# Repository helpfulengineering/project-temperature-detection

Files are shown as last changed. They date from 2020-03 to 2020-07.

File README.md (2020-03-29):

# Hardware temperature detection project

Project to build a simple, cheap, open source fever detection device. The aim is to allow symptomatic people to be quickly isolated.

On slack channel [#hardware-temperature-detection](https://app.slack.com/client/TUTSYURT3/CVCEV2V0V/thread/CV96HC6DN-1584885987.479600) from [helpfulengineering.slack.com](https://helpfulengineering.slack.com/)

Fast fever detection followed by isolation reduces the spread of infectious diseases.

## User Experience

Journey a user goes through to use the system
Initial idea is represented in the picture, taking the user from the first interface with the device to the result feedback. 
It assumes the mirror alignment but does not go into detail about it yet. 
It also lacks the user experience after the outcome communication. 

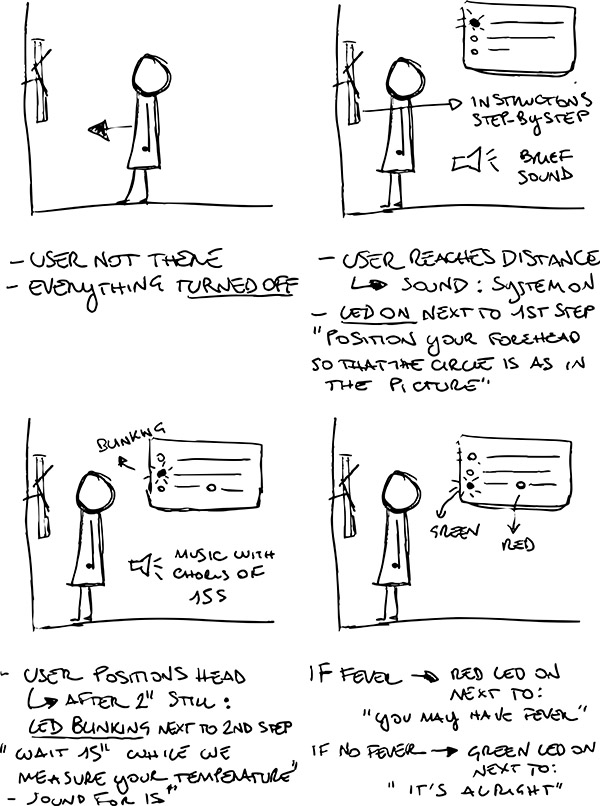
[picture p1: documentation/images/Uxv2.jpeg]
UX


## Functional diagram

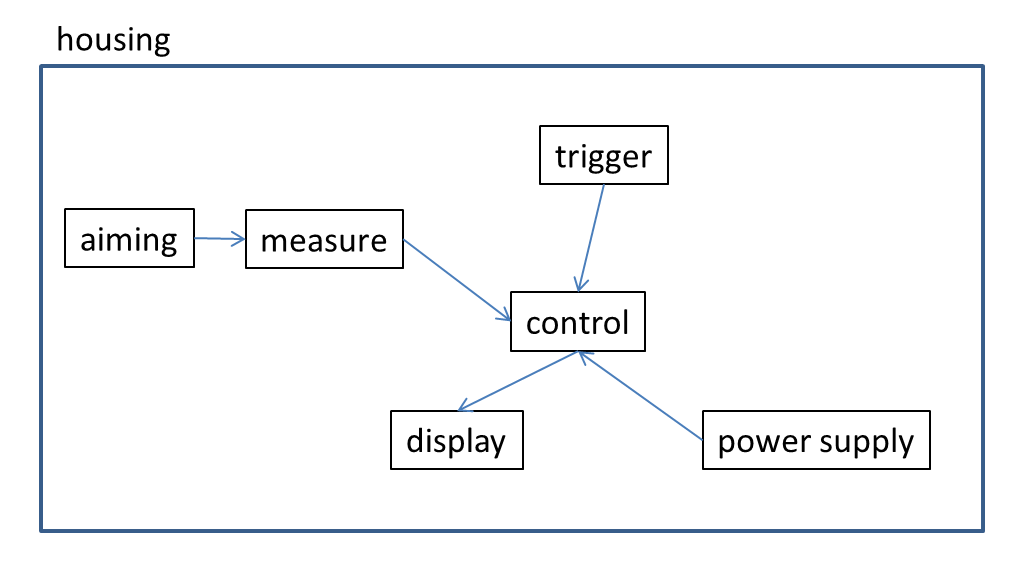
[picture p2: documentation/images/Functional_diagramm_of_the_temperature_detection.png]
diagram


## [Project wiki](https://github.com/helpfulengineering/project-temperature-detection/wiki)

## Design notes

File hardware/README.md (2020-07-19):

# PCB and parts

### parts
- temperature sensor MLX90614
- acoustic range find sensor - generic Hc-SR04
- 10mm LEDs generic
- Arduino UNO

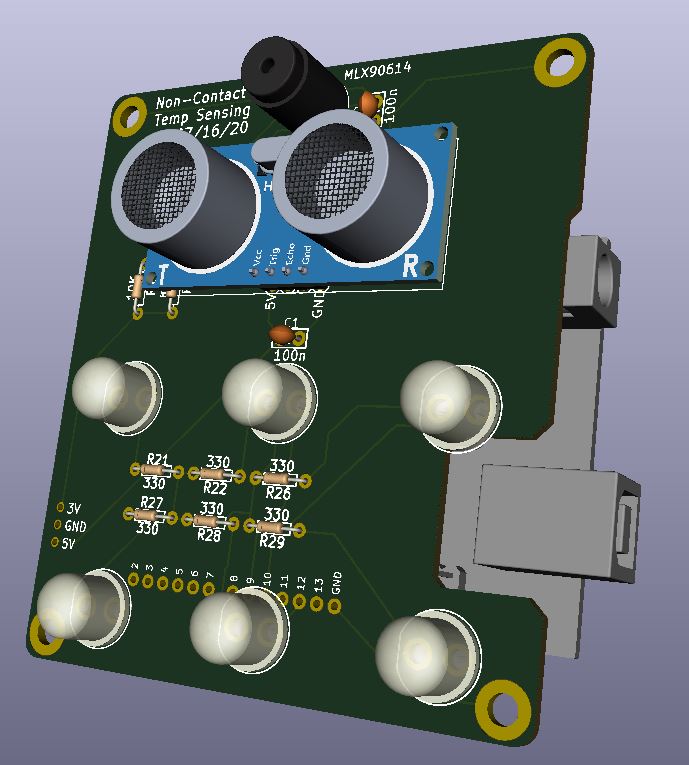
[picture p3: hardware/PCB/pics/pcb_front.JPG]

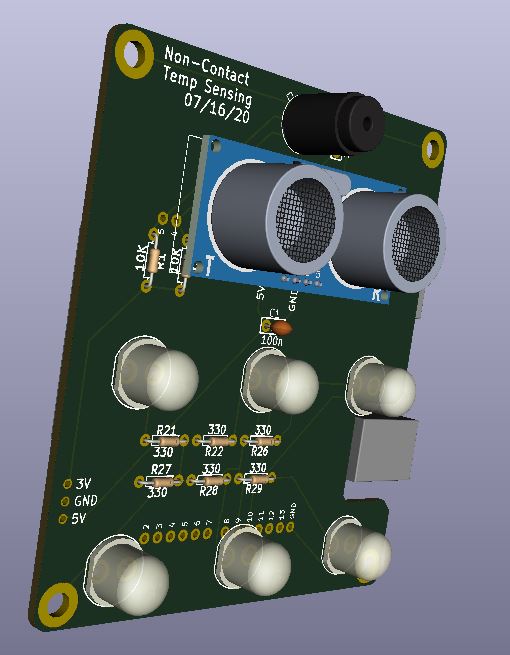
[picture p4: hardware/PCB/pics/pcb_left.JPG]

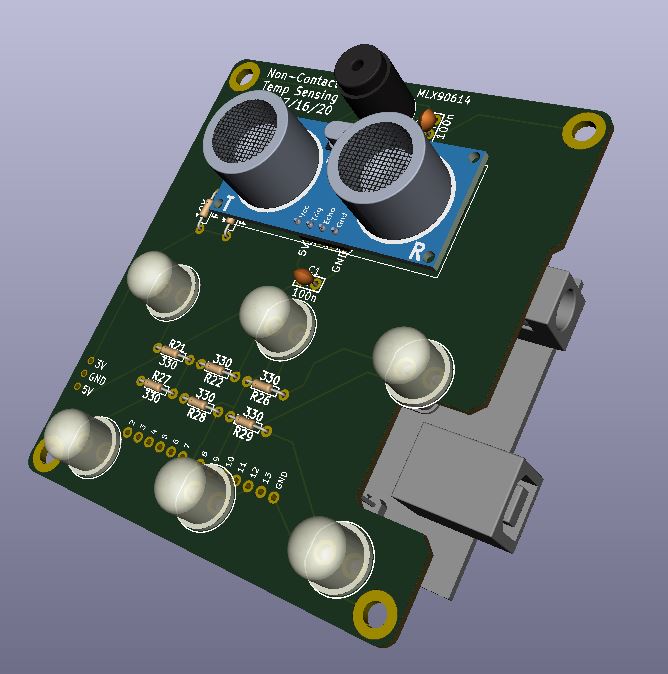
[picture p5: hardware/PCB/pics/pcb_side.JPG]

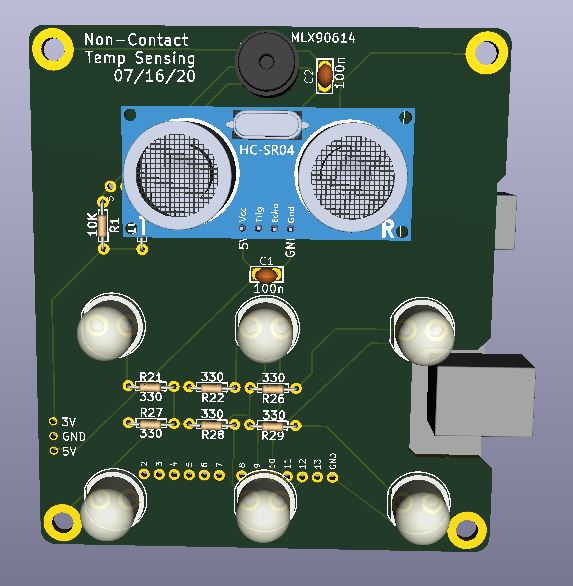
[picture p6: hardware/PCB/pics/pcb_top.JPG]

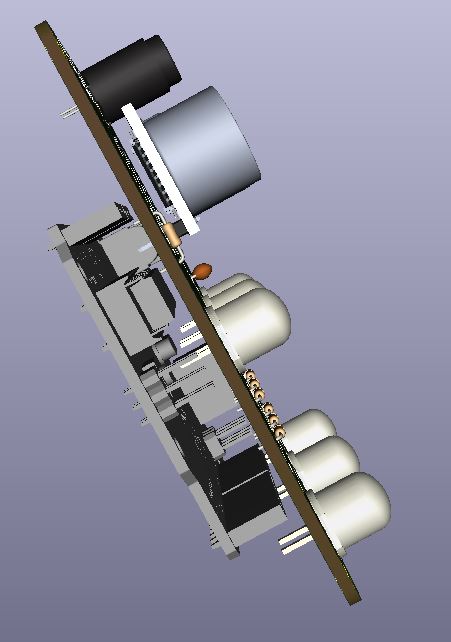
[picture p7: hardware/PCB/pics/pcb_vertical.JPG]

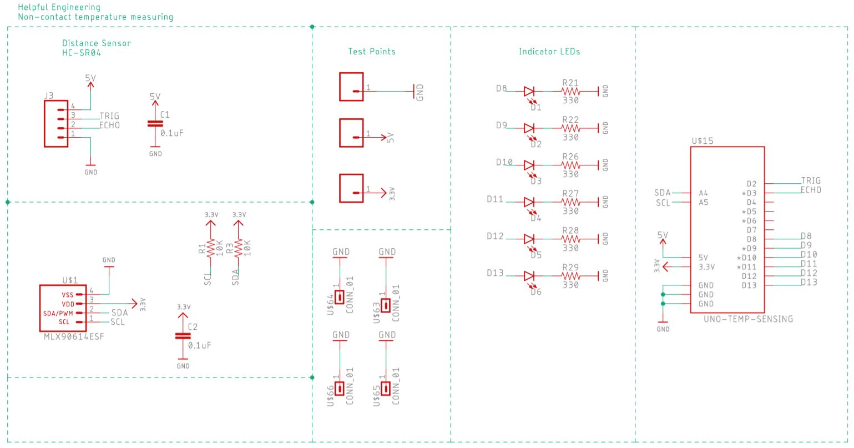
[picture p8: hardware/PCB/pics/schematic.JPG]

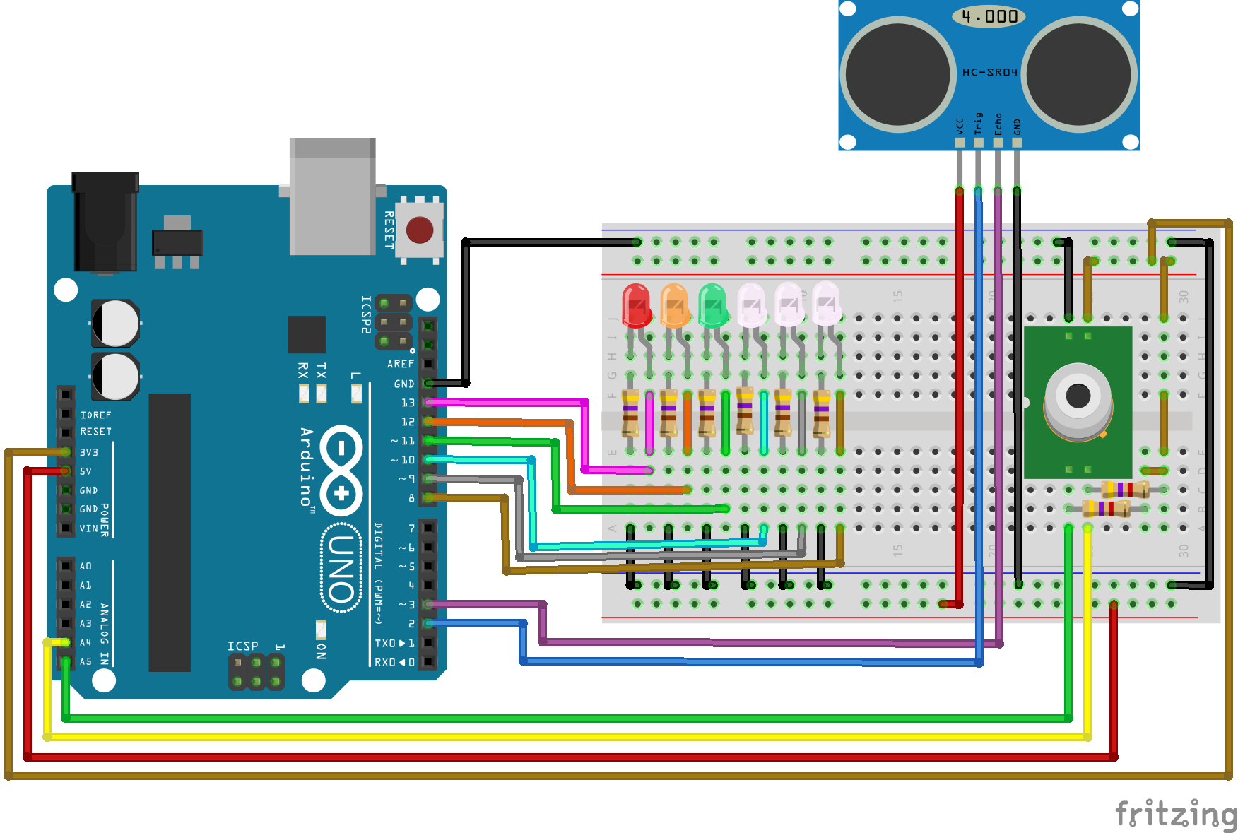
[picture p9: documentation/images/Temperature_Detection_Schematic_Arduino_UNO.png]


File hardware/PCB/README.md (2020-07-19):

# PCB in Eagle

The current printed circuit board was designed in Eagle and imported into kicad for 3d renderings

foo

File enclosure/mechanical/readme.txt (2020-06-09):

Laser cut all parts
Material: Acrylic 
Thickness: 3mm. (1/8" works too)
Adhesive base panel to side panels with acrylic cement or acrylic glue.
On the clear part, the red line is for etching.
All parts were designed to fit on a Glowforge laser cutter

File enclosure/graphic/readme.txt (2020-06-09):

print this on white paper, cut along the red line, laminate it, cut as close to edge as possible. Tape along top and bottom edges against the INSIDE of the clear window (use the etched border of the clear window as a positioning guide).

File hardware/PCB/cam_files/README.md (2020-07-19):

# Hardware temperature detection project - cam files

These are the files required for MFG the PCB. Upload the files to a board house like [JLCPCB.com](https://jlcpcb.com/).

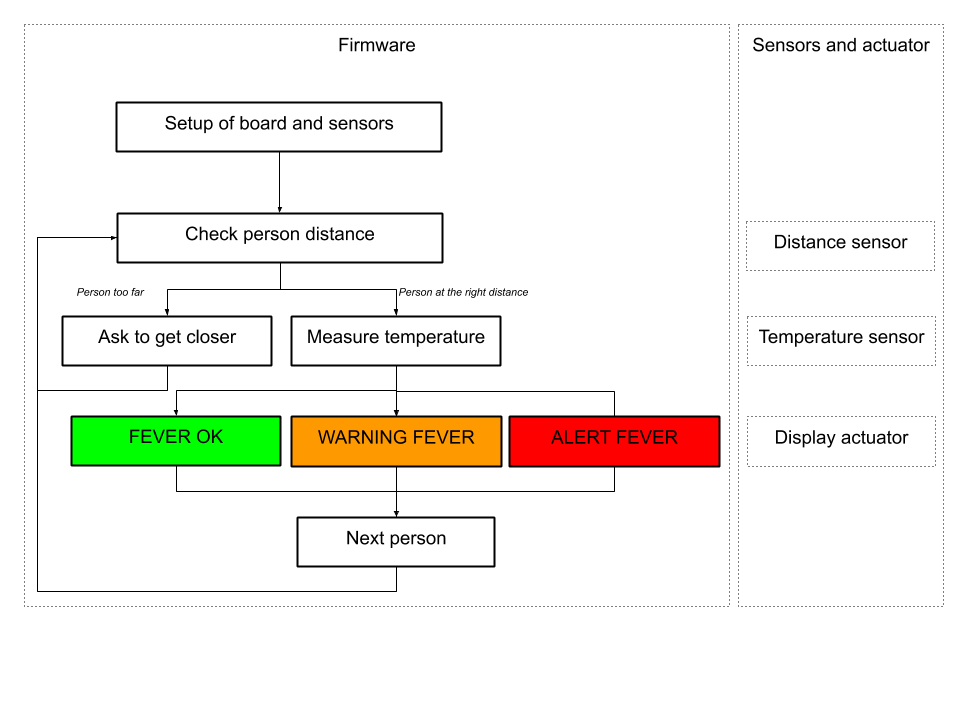
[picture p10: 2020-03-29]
documentation/images/Temperature check software algorithm.png

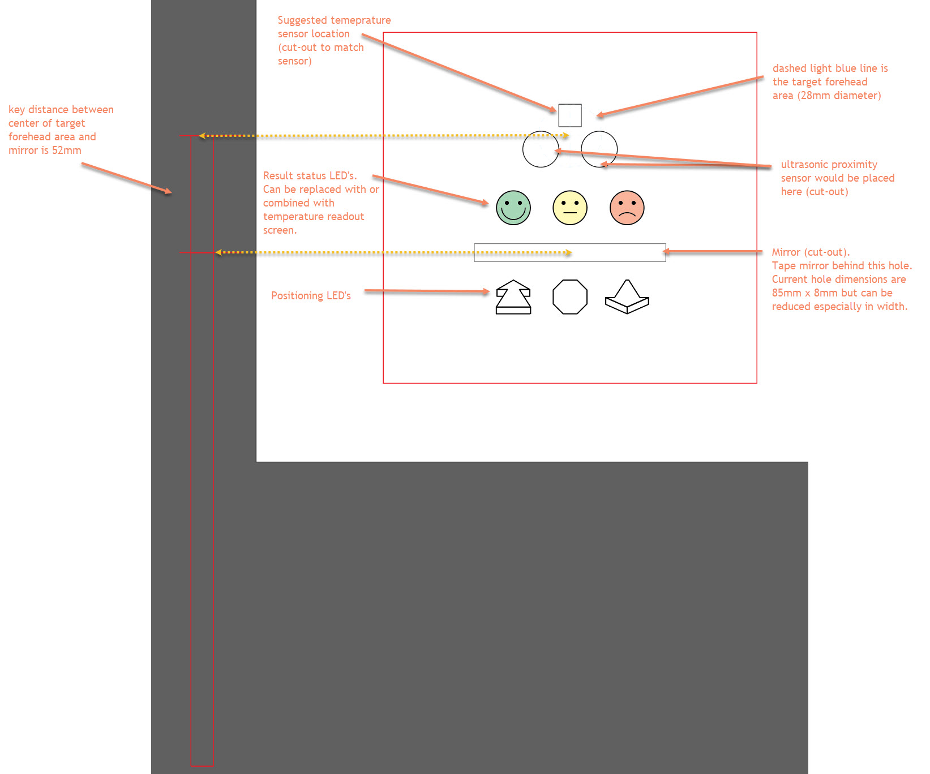
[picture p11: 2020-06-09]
enclosure/graphic/readme.jpg

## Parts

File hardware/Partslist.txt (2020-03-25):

Circuit.io https://www.circuito.io/app?components=512,9570,9590,9590,9591,9591,9594,11021,13959
Parts list with price estimates for design without a viewfinder.
Arduino Uno
$23.38 x Qty: 1

Infrared Thermometer - MLX90614
$14.78 x Qty: 1

4.7K Ohm Resistor
$0.1 x Qty: 2

Capacitor Ceramic 100nF
$0.64 x Qty: 1

USB Cable A to B
$3.26 x Qty: 1

LED - Basic Green 5mm
$0.33 x Qty: 2

330 Ohm Resistor
$0.1 x Qty: 2

Ultrasonic Sensor - HC-SR04
$3.95 x Qty: 1

LED - Basic Yellow 5mm
$0.35 x Qty: 1

220 Ohm Resistor
$0.1 x Qty: 3

LED - Basic Red 5mm
$0.36 x Qty: 2

BreadBoard
$8.25 x Qty: 1

Jumper Wires Pack - M/M
$1.95 x Qty: 2

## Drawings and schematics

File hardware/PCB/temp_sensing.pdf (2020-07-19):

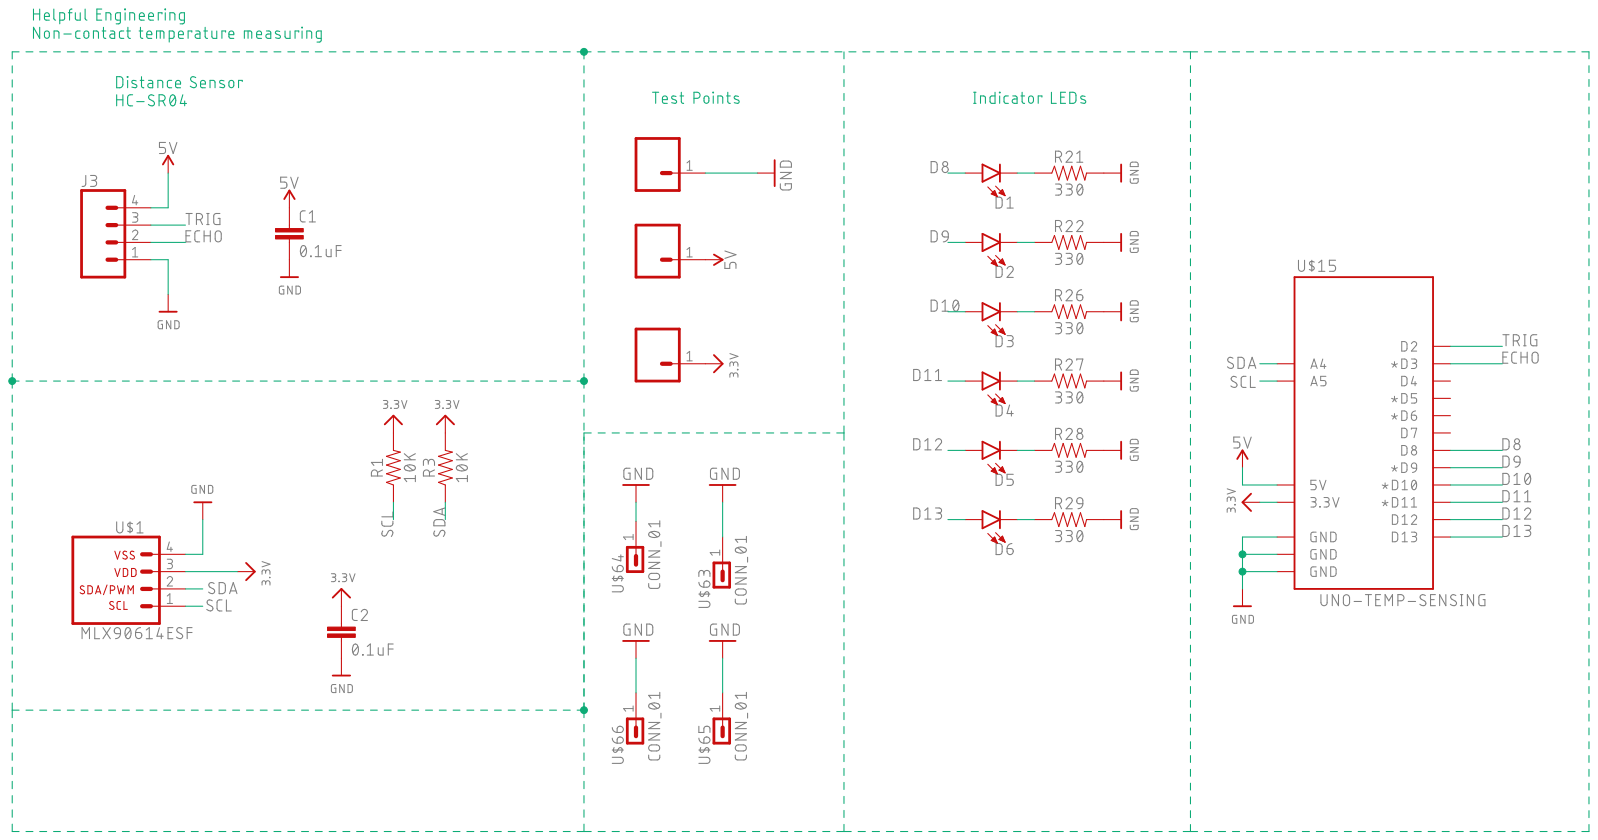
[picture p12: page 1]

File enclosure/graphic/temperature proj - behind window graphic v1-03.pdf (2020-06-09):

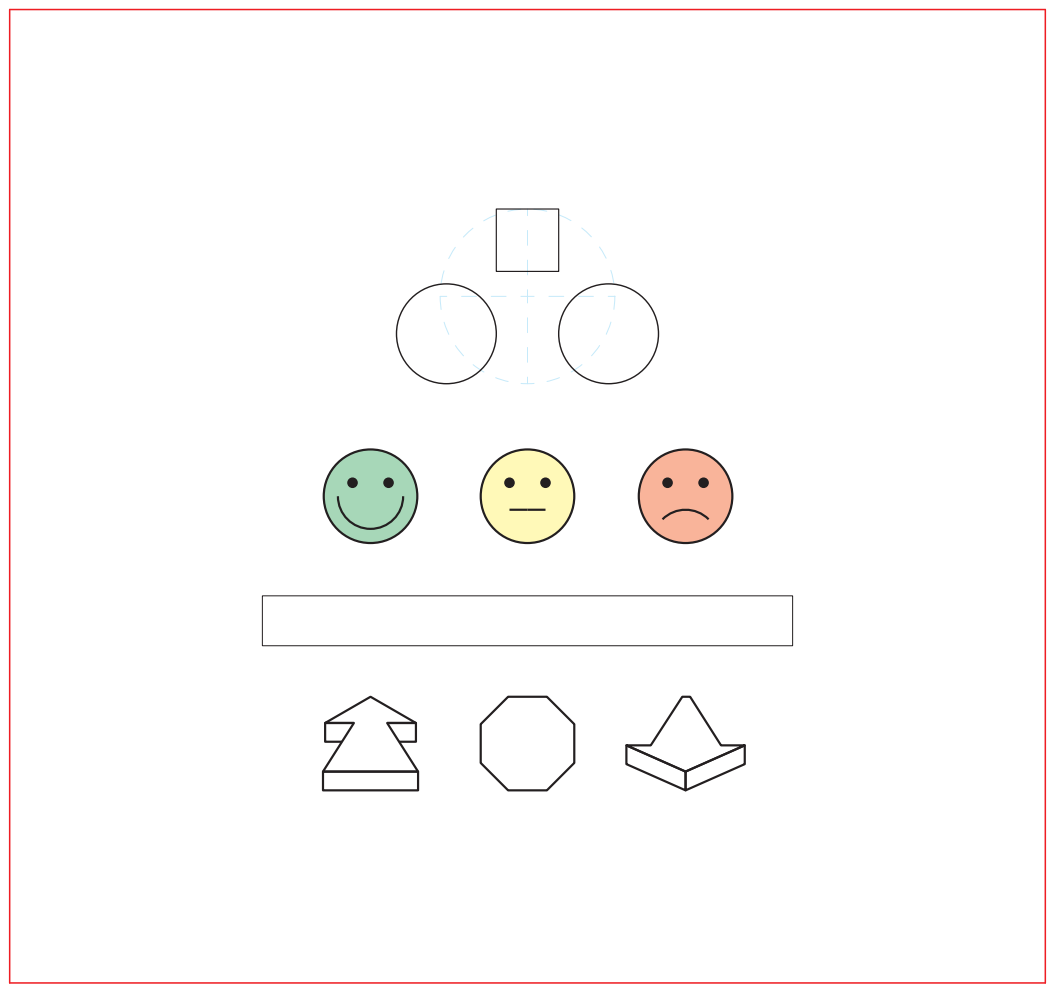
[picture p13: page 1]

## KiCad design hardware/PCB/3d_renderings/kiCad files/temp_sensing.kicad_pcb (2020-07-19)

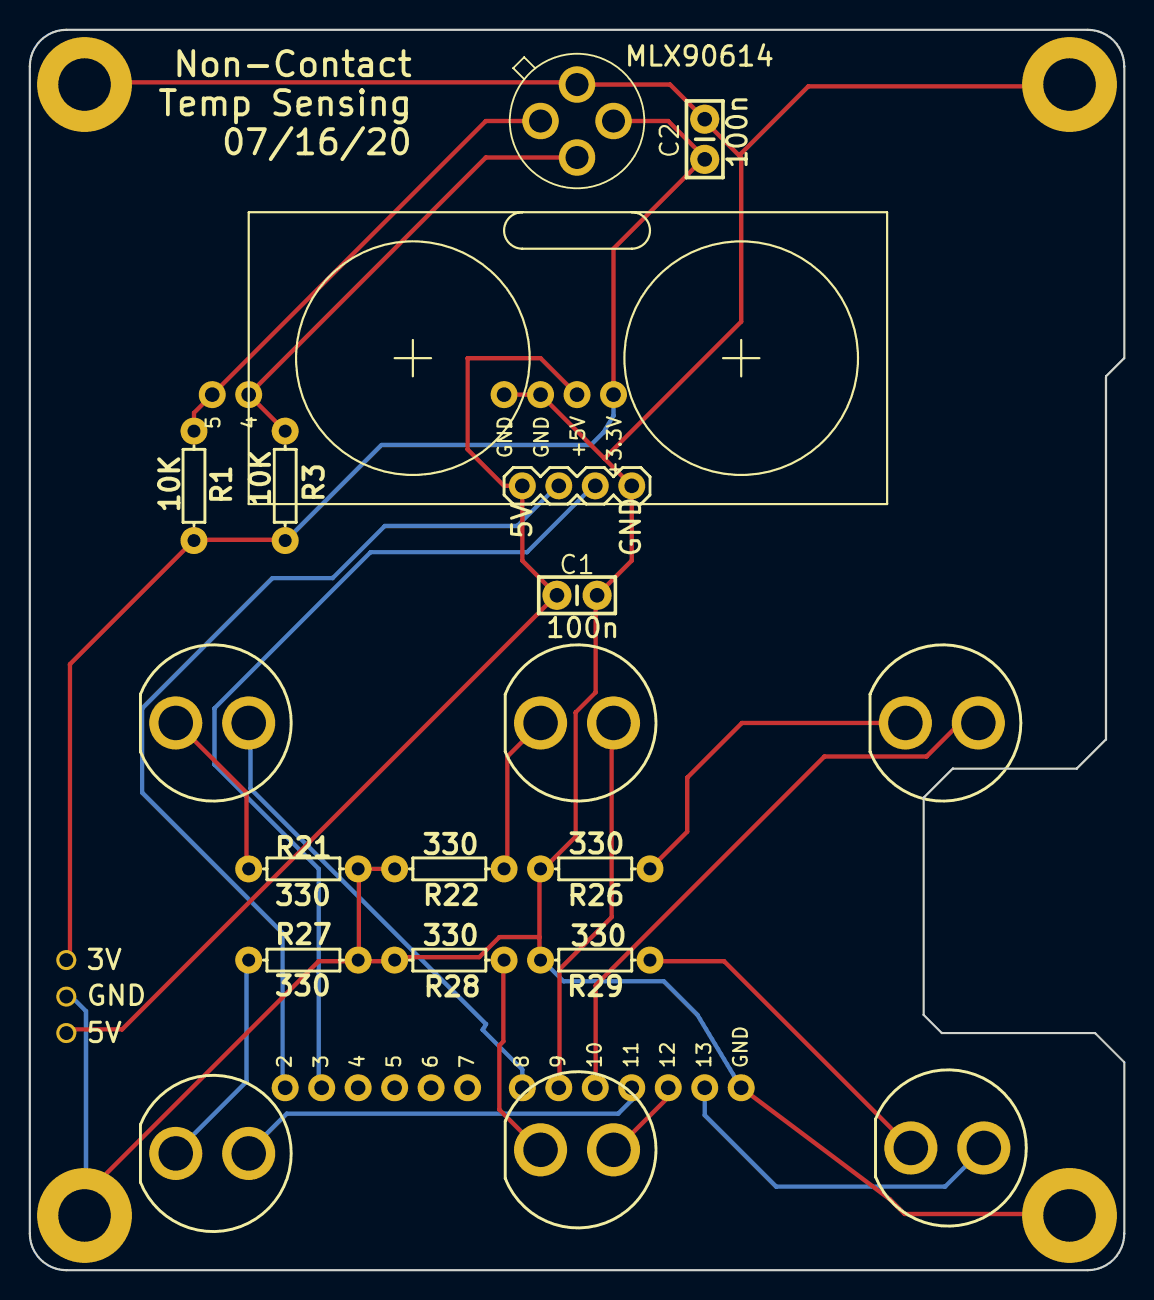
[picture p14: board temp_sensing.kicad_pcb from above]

Board: 2 copper layers, 76.2 x 86.4 mm, 26 parts (0 on the bottom side), 19 nets.

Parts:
C1, C2: 0.1uF; CAP-PTH-SMALL-KIT
D1, D2, D3, D4, D5, D6: LED10MM; LED_10MM
J3: CONN_04PTH; 1X04
R1, R3: 10K; AXIAL-0.3
R21, R22, R26, R27, R28, R29: 330; AXIAL-0.3
U$1: MLX90614ESF; MLX90614XCI
U$15: UNO-TEMP-SENSING; UNO_FOOTRPINT
U$20, U$31, U$59: CONN_0138MILL; 1X01-40MILL
U$63, U$64, U$65, U$66: CONN_01; 1X01-#6_MACHINE

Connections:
3.3V: C2.1, R1.P$2, R3.P$2, U$1.3, U$15.3.3V, U$20.1
5V: C1.1, J3.4, U$15.5V, U$59.1
/D8: D1.A, U$15.D8
/D9: D2.A, U$15.D9
/D10: D3.A, U$15.D10
/D11: D4.A, U$15.D11
/D12: D5.A, U$15.D12
/D13: D6.A, U$15.D13
/ECHO: J3.2, U$15.D3
/SCL: R1.P$1, U$1.1, U$15.A5
/SDA: R3.P$1, U$1.2, U$15.A4
/TRIG: J3.3, U$15.D2
GND: C1.2, C2.2, J3.1, R21.P$2, R22.P$2, R26.P$2, R27.P$2, R28.P$2, R29.P$2, U$1.4, U$15.GND@0, U$15.GND@1, U$15.GND@2, U$31.1, U$63.1, U$64.1, U$65.1, U$66.1
unnamed: D1.C, R21.P$1
unnamed: D2.C, R22.P$1
unnamed: D3.C, R26.P$1
unnamed: D4.C, R27.P$1
unnamed: D5.C, R28.P$1
unnamed: D6.C, R29.P$1

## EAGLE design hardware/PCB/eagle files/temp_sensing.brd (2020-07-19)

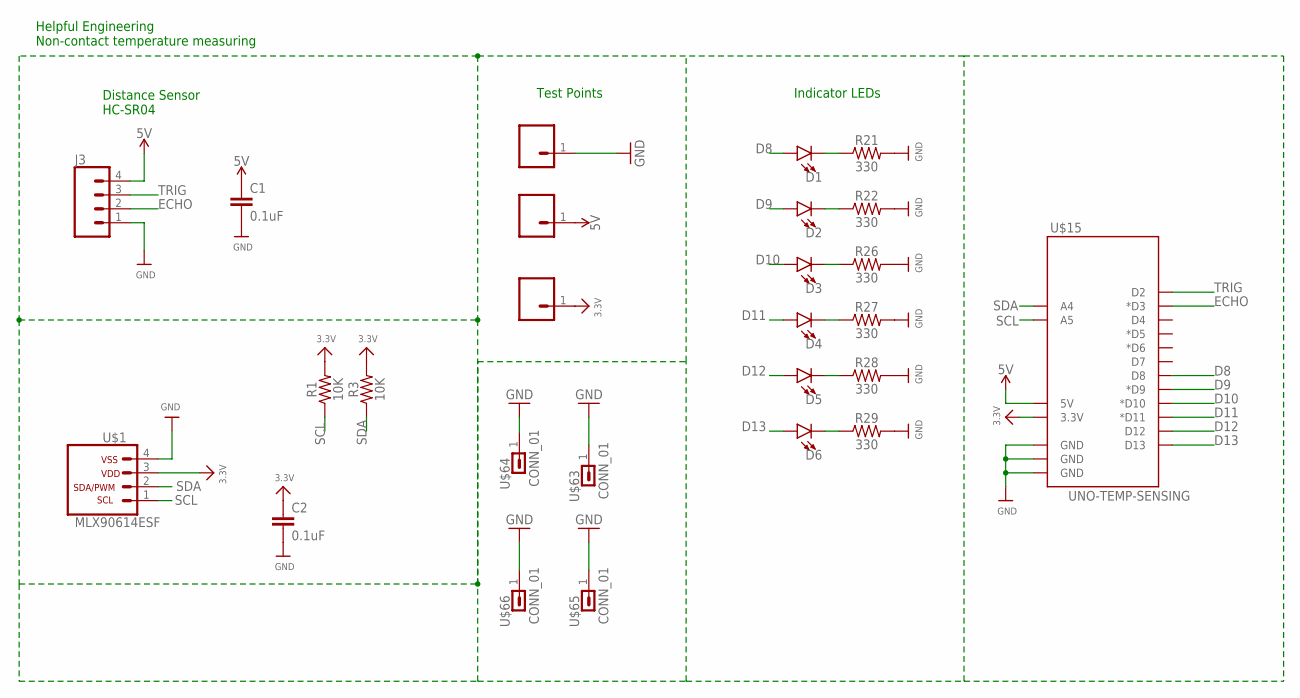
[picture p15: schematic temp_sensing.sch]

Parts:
C1, C2: 0.1uF; CAP-PTH-SMALL-KIT
D1, D2, D3, D4, D5, D6: LED10MM; LED_10MM
J3: CONN_04PTH; 1X04
R1, R3: 10K; AXIAL-0.3
R21, R22, R26, R27, R28, R29: 330; AXIAL-0.3
U$1: MLX90614ESF; MLX90614XCI
U$15: UNO-TEMP-SENSING; UNO_FOOTRPINT
U$20, U$31, U$59: CONN_0138MILL; 1X01-40MILL
U$63, U$64, U$65, U$66: CONN_01; 1X01-#6_MACHINE

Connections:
3.3V: C2.1, R1.P$2 (2), R3.P$2 (2), U$1.3, U$15.3.3V, U$20.1
5V: C1.1, J3.4, U$15.5V, U$59.1
D8: D1.A, U$15.D8
D9: D2.A, U$15.D9 (*D9)
D10: D3.A, U$15.D10 (*D10)
D11: D4.A, U$15.D11 (*D11)
D12: D5.A, U$15.D12
D13: D6.A, U$15.D13
ECHO: J3.2, U$15.D3 (*D3)
GND: C1.2, C2.2, J3.1, R21.P$2 (2), R22.P$2 (2), R26.P$2 (2), R27.P$2 (2), R28.P$2 (2), R29.P$2 (2), U$1.4, U$15.GND@0 (GND), U$15.GND@1 (GND), U$15.GND@2 (GND), U$31.1, U$63.1, U$64.1, U$65.1, U$66.1
unnamed: D6.C, R29.P$1 (1)
unnamed: D1.C, R21.P$1 (1)
unnamed: D2.C, R22.P$1 (1)
unnamed: D3.C, R26.P$1 (1)
unnamed: D4.C, R27.P$1 (1)
unnamed: D5.C, R28.P$1 (1)
SCL: R1.P$1 (1), U$1.1, U$15.A5
SDA: R3.P$1 (1), U$1.2, U$15.A4
TRIG: J3.3, U$15.D2

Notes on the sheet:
Test Points
Indicator LEDs
Helpful Engineering Non-contact temperature measuring
Distance Sensor HC-SR04

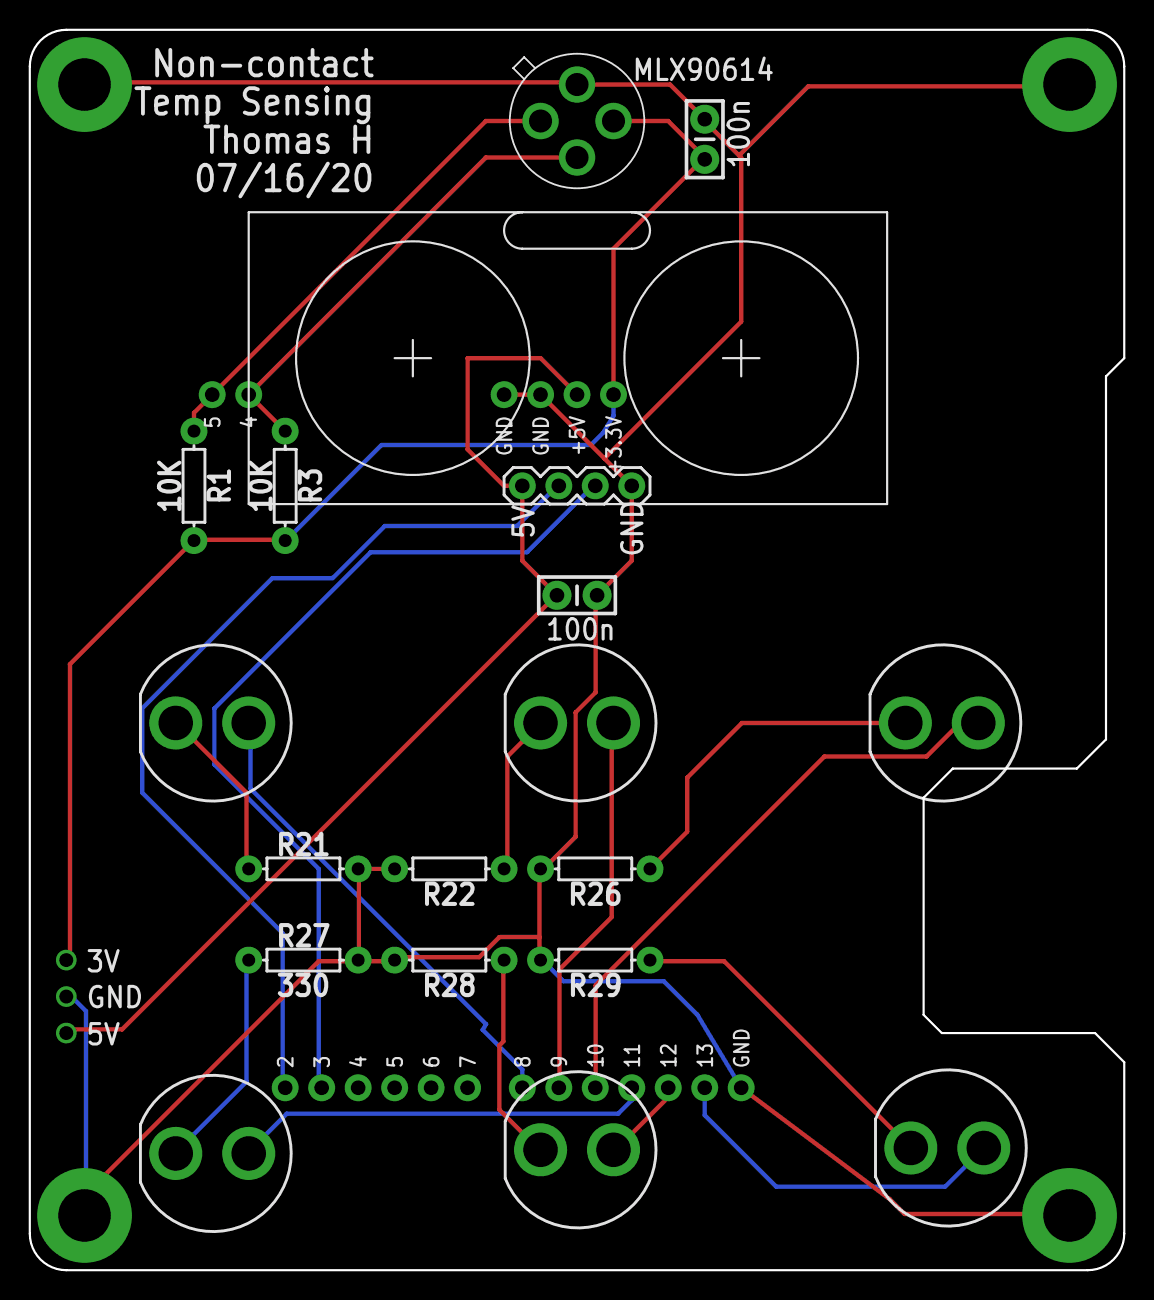
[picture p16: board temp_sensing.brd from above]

Board: 2 copper layers, 76.2 x 86.4 mm, 26 parts (0 on the bottom side), 19 nets.

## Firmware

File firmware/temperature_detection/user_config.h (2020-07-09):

#ifndef USER_CONFIG_H
#define USER_CONFIG_H

// Switches
// #define ENABLE_SONAR
// #define INVERT_INDICATORS
// #define SENSOR_ZTP115M // See also ZTP115M_SENSOR_* defines
#define SENSOR_MLX90614


// Boards
// #define M5STICKC
// #define ANOTHER

#ifdef M5STICKC
    #define ENABLE_BUTTON
    #define INVERT_INDICATORS
    #undef ENABLE_INDICATORS
    #undef ENABLE_SONAR
#endif

#ifdef ANOTHER
    #define ENABLE_BUTTON
    #define ENABLE_INDICATORS
    #define ENABLE_SONAR
#endif

// Times (bauds and milliseconds)
#define SERIAL_MONITOR_SPEED        115200
#define SENSOR_STABILIZATION_TIME   100
#define TIME_BETWEEN_READINGS       500
#define DISPLAY_TIME                2000

// Sampling (count and milliseconds)
#define TEMPERATURE_SAMPLES         3
#define TEMPERATURE_INTERVAL        500
#define DISTANCE_SAMPLES            5
#define DISTANCE_INTERVAL           100 // >60 as per Sparkfun HC-SR04 datasheet

// Distances (centimeters)
#define OFF_DISTANCE                100
#define THRESHOLD_DISTANCE          7
#define DETECTION_DISTANCE          3

// Temperatures (celsius degrees)
#define LIMIT_FEVER                 33
#define WARNING_FEVER               31

// Pins
#ifndef ULTRASOUND_TRIGGER_PIN
#define ULTRASOUND_TRIGGER_PIN      2
#endif
#ifndef ULTRASOUND_ECHO_PIN
#define ULTRASOUND_ECHO_PIN         3
#endif
#ifndef TEMPERATURE_LOW_PIN
#define TEMPERATURE_LOW_PIN         11
#endif
#ifndef TEMPERATURE_MID_PIN
#define TEMPERATURE_MID_PIN         12
#endif
#ifndef TEMPERATURE_HIGH_PIN
#define TEMPERATURE_HIGH_PIN        13
#endif
#ifndef DISTANCE_FARTHER_PIN
#define DISTANCE_FARTHER_PIN        8 // FIXME: why skip the seventh pin?
#endif
#ifndef DISTANCE_STOP_PIN
#define DISTANCE_STOP_PIN           10
#endif
#ifndef DISTANCE_CLOSER_PIN
#define DISTANCE_CLOSER_PIN         9
#endif
#ifndef BUTTON_PIN
#define BUTTON_PIN                  7 // 37 to use BUTTON A on M5StickC
#endif
#ifndef ZTP115M_SENSOR_PIN
#define ZTP115M_SENSOR_PIN          36
#endif
#ifdef ESP32
#define ESP32_SDA_PIN               0
#define ESP32_SCL_PIN               26
#endif

// ZTP115M-specific ADC settings
#ifdef ESP32

#ifndef ZTP115M_SENSOR_REFERENCE
#define ZTP115M_SENSOR_REFERENCE    3.3
#endif
#ifndef ZTP115M_SENSOR_STEPS
#define ZTP115M_SENSOR_STEPS        4096
#endif

#else

#ifndef ZTP115M_SENSOR_REFERENCE
#define ZTP115M_SENSOR_REFERENCE    5
#endif
#ifndef ZTP115M_SENSOR_STEPS
#define ZTP115M_SENSOR_STEPS        1024 // Might not offer enough resolution.
#endif

#endif

#endif

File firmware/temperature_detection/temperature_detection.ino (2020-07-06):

#include "user_config.h"
#include <Adafruit_MLX90614.h>
#ifdef M5STICKC
#include <M5StickC.h>
#endif

typedef enum {
    INDICATOR_TEMPERATURE_LOW  = 1 << 0,
    INDICATOR_TEMPERATURE_MID  = 1 << 1,
    INDICATOR_TEMPERATURE_HIGH = 1 << 2,
    INDICATOR_DISTANCE_FARTHER = 1 << 3,
    INDICATOR_DISTANCE_STOP    = 1 << 4,
    INDICATOR_DISTANCE_CLOSER  = 1 << 5
} indicator;

typedef enum {
    STATUS_OFF     = 0,
    STATUS_TRIGGER = INDICATOR_DISTANCE_STOP,
    STATUS_FEVER_LOW  = INDICATOR_TEMPERATURE_LOW,
    STATUS_FEVER_MID  = INDICATOR_TEMPERATURE_MID,
    STATUS_FEVER_HIGH = INDICATOR_TEMPERATURE_HIGH,
    STATUS_DISTANCE_FARTHER = INDICATOR_DISTANCE_FARTHER,
    STATUS_DISTANCE_STOP    = INDICATOR_DISTANCE_STOP,
    STATUS_DISTANCE_CLOSER  = INDICATOR_DISTANCE_CLOSER
} status;


float measure_temperature_ztp115m();
float measure_temperature_mlx90614();
float measure_temperature(size_t samples, int interval);
int measure_distance(size_t samples, int interval);
void await_status(status desired_status);
void display_status(status indicators);
status detect_user();


void setup() {
    Serial.begin(SERIAL_MONITOR_SPEED);

    #ifdef ENABLE_SONAR
        pinMode(ULTRASOUND_ECHO_PIN, INPUT);
        pinMode(ULTRASOUND_TRIGGER_PIN, OUTPUT);
    #endif

    #ifdef ENABLE_INDICATORS
        pinMode(TEMPERATURE_LOW_PIN, OUTPUT);
        pinMode(TEMPERATURE_MID_PIN, OUTPUT);
        pinMode(TEMPERATURE_HIGH_PIN, OUTPUT);
        pinMode(DISTANCE_FARTHER_PIN, OUTPUT);
        pinMode(DISTANCE_STOP_PIN, OUTPUT);
        pinMode(DISTANCE_CLOSER_PIN, OUTPUT);
    #endif

    #ifdef ENABLE_BUTTON
        pinMode(BUTTON_PIN, INPUT_PULLUP);
    #endif

    #ifdef M5STICKC
        M5.begin();
    #endif

    #ifdef ESP32
        Wire.begin(ESP32_SDA_PIN, ESP32_SCL_PIN);
    #endif

    Serial.println("Setup complete");
}


void loop() {
    await_status(STATUS_TRIGGER);
    delay(SENSOR_STABILIZATION_TIME);

    float temperature = measure_temperature(
        TEMPERATURE_SAMPLES,
        TEMPERATURE_INTERVAL
    );

    Serial.println("Temperature (in celsius degrees): ");
    Serial.println(temperature);

    if(temperature > LIMIT_FEVER) {
        display_status(STATUS_FEVER_HIGH);
        Serial.println("Fever detected");
    } else if(temperature > WARNING_FEVER) {
        display_status(STATUS_FEVER_MID);
        Serial.println("Fever probably detected");
    } else {
        display_status(STATUS_FEVER_LOW);
        Serial.println("No fever detected");
    }

    delay(DISPLAY_TIME);
    await_status(STATUS_OFF);
}


void await_status(status desired_status) {
    status current_status;

    do {
        current_status = (
            (digitalRead(BUTTON_PIN) == LOW)
            ? STATUS_TRIGGER : detect_user()
        );
        display_status(current_status);
    } while(current_status != desired_status);
}


status detect_user() {
    #ifdef ENABLE_SONAR
        int distance = measure_distance(
            DISTANCE_SAMPLES,
            DISTANCE_INTERVAL
        );

        Serial.println("Distance (in centimeters): ");
        Serial.println(distance);

        if (distance > OFF_DISTANCE) {
            Serial.println("User is not present");
            return STATUS_OFF;
        } else if (distance > DETECTION_DISTANCE + THRESHOLD_DISTANCE / 2) {
            Serial.println("User needs to get closer");
            return STATUS_DISTANCE_CLOSER;
        } else if (distance < DETECTION_DISTANCE - THRESHOLD_DISTANCE / 2) {
            Serial.println("User needs to get farther");
            return STATUS_DISTANCE_FARTHER;
        } else {
            Serial.println("User is at a good distance; stay still");
            return STATUS_DISTANCE_STOP;
        }
    #else
        return STATUS_OFF;
    #endif
}


int measure_distance(size_t samples, int interval) {
    float measurements = 0;
    for(size_t counter = 0; counter < (samples || 1); counter++) {
        digitalWrite(ULTRASOUND_TRIGGER_PIN, LOW);
        delayMicroseconds(2);
        digitalWrite(ULTRASOUND_TRIGGER_PIN, HIGH);
        delayMicroseconds(10);
        digitalWrite(ULTRASOUND_TRIGGER_PIN, LOW);

        long duration = pulseIn(ULTRASOUND_ECHO_PIN, HIGH);
        measurements += duration * 0.034 / 2;

        delay(interval);
    }
    return measurements / (samples || 1); // centimeters
}


float measure_temperature(size_t samples, int interval) {
    float measurements = 0;
    for(size_t counter = 0; counter < (samples || 1); counter++) {
        #if defined(SENSOR_MLX90614)
            measurements += measure_temperature_mlx90614();
        #elif defined(SENSOR_ZTP115M) && defined(ZTP115M_SENSOR_PIN)
            measurements += measure_temperature_ztp115m();
        #else
            #error No sensor specified!
        #endif
        delay(interval);
    }
    return measurements / (samples || 1); // celsius degrees
}


float measure_temperature_ztp115m() {
    int value = analogRead(ZTP115M_SENSOR_PIN);
    float voltage = ZTP115M_SENSOR_REFERENCE * (value / ZTP115M_SENSOR_STEPS);
    return (
        - 3484.051933 * pow(voltage, 0)
        + 11296.70621 * pow(voltage, 1)
        - 15853.08557 * pow(voltage, 2)
        + 12490.72137 * pow(voltage, 3)
        - 5998.724365 * pow(voltage, 4)
        + 1797.550087 * pow(voltage, 5)
        - 328.5445919 * pow(voltage, 6)
        + 33.53566265 * pow(voltage, 7)
        - 1.465912126 * pow(voltage, 8)
    );
}


float measure_temperature_mlx90614() {
    static Adafruit_MLX90614 temperature_sensor = Adafruit_MLX90614();
    #ifndef ESP32
        temperature_sensor.begin();
    #endif
    return temperature_sensor.readObjectTempC();
}


void display_status(status indicators) {
    #ifdef INVERT_INDICATORS
        indicators = (status)~indicators;
    #endif
    #ifdef M5STICKC
        M5.Lcd.fillRect(0, 0, 40, 53,
            (indicators & INDICATOR_TEMPERATURE_HIGH)
            ? TFT_RED : TFT_BLACK
        );
        M5.Lcd.fillRect(0, 53, 40, 53,
            (indicators & INDICATOR_TEMPERATURE_MID)
            ? TFT_ORANGE : TFT_BLACK
        );
        M5.Lcd.fillRect(0, 106, 40, 54,
            (indicators & INDICATOR_TEMPERATURE_LOW)
            ? TFT_GREEN : TFT_BLACK
        );
        M5.Lcd.fillRect(40, 0, 80, 53,
            (indicators & INDICATOR_DISTANCE_FARTHER)
            ? TFT_ORANGE : TFT_BLACK
        );
        M5.Lcd.fillRect(40, 53, 80, 53,
            (indicators & INDICATOR_DISTANCE_STOP)
            ? TFT_GREEN : TFT_BLACK
        );
        M5.Lcd.fillRect(40, 106, 80, 54,
            (indicators & INDICATOR_DISTANCE_CLOSER)
            ? TFT_ORANGE : TFT_BLACK
        );
    #endif
    digitalWrite(
        TEMPERATURE_HIGH_PIN,
        (indicators & INDICATOR_TEMPERATURE_HIGH)
        ? HIGH : LOW
    );
    digitalWrite(
        TEMPERATURE_MID_PIN,
        (indicators & INDICATOR_TEMPERATURE_MID)
        ? HIGH : LOW
    );
    digitalWrite(
        TEMPERATURE_LOW_PIN,
        (indicators & INDICATOR_TEMPERATURE_LOW)
        ? HIGH : LOW
    );
    digitalWrite(
        DISTANCE_FARTHER_PIN,
        (indicators & INDICATOR_DISTANCE_FARTHER)
        ? HIGH : LOW
    );
    digitalWrite(
        DISTANCE_STOP_PIN,
        (indicators & INDICATOR_DISTANCE_STOP)
        ? HIGH : LOW
    );
    digitalWrite(
        DISTANCE_CLOSER_PIN,
        (indicators & INDICATOR_DISTANCE_CLOSER)
        ? HIGH : LOW
    );
}

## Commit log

2020-03-25 circuit diagram
2020-03-25 Update Partslist.txt
    added circuit.io link
2020-04-02 Handle float instead of int for temperatures
    As we would like to be close as possible to the sensor accuracy we will handle float instead of in
2020-04-04 Code cleanup (#7)
    * Code cleanup
    * Update firmware/temperature_detection/temperature_detection.ino
    * Externalize constant to a .h file
    Fever indcator pin is not used
    so remove it
    * Add logs to make the debugging easier
    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
2020-04-06 Add UNO schematic
    [Temperature_Detection_Arduino_UNO.fzz]
2020-04-06 Straighten a few wires
    [Temperature_Detection_Arduino_UNO.fzz]
2020-04-07 Add missing resistors (#11)
    * Add missing resistors
    * Fix the logic level of the pull resistors
    [Temperature_Detection_Arduino_UNO.fzz]
2020-04-14 Add average measurements (#9)
    * Add average measurements
    * Replace the 0 constraint by a more elegant ||
    * Update temperature_detection.ino
    * Add intervals to function calls and user_config.h
2020-04-25 Allow a button to trigger measurements in devices without sonar (#13)
    * Modularize trigger function
    * Complete M5StickC board specific parameters
    * Add traces
    * Change limit fever to 30 so as to be able to test with the skin temperature
    * Set stabilization time macro to 100ms
2020-06-04 added code for converting voltage to temperature for ztp-115m (#15)
    * Add support for ZTP115M
    * Add configuration for ZTP115M
    * Add customizable ADC steps
2020-06-05 Add LCD color display to M5StickC (#16)
    * Add LCD color display to M5StickC
    Display simple colors instead of led usage (RED/GREEN)
    RED when fever is detected after a button push
    GREEN when there is no fever after a button push
    * Allow combined statuses
    * Restore permanent support for LED indicators
    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
2020-07-07 Correct logic for boards definition (#18)
    and set the serial monitor speed on platformio.ini file
    change the serial speed to 115200
2020-07-09 Change pins and parameters according to the prototype (#19)
    [Temperature_Detection_Arduino_UNO.fzz]
2020-07-19 PCB files and 3d rendering (#20)
    * updated PCB cad files and 3d rendering
    * added kicad files
    * fixed images
    [temp_sensing.brd, temp_sensing.kicad_pcb, temp_sensing.sch]

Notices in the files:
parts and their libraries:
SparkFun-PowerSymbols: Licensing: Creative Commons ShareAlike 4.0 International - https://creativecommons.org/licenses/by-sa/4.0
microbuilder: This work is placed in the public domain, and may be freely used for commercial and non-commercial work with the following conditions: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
